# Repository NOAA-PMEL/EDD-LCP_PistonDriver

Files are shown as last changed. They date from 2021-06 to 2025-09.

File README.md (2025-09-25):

## Legal Disclaimer
### Software Disclaimer
*This repository is a software product and is not official communication 
of the National Oceanic and Atmospheric Administration (NOAA), or the 
United States Department of Commerce (DOC).  All NOAA GitHub project 
code is provided on an 'as is' basis and the user assumes responsibility 
for its use.  Any claims against the DOC or DOC bureaus stemming from 
the use of this GitHub project will be governed by all applicable Federal 
law.  Any reference to specific commercial products, processes, or services 
by service mark, trademark, manufacturer, or otherwise, does not constitute 
or imply their endorsement, recommendation, or favoring by the DOC. 
The DOC seal and logo, or the seal and logo of a DOC bureau, shall not 
be used in any manner to imply endorsement of any commercial product 
or activity by the DOC or the United States Government.*

### Hardware Disclaimer
*NOAA does not intend to patent this work worldwide. It may be used freely, but NOAA does not warrant its fitness for any use.*

*As a work of the United States Government, the associated schematics and software are in the public domain within the United States. Additionally, NOAA waives any potential copyright and related rights in the associated schematics and software worldwide through the Creative Commons Zero (CC0) 1.0 Universal Public Domain Declaration.*

# EDD-LCP_PistonDriver
Repository for LCP Piston Driver PCB design and firmware.

This repository is home to the piston driver PCB design and firmware for the low-cost-profiler project (likely to be renamed).

## State of this project
The LCP has been extensilivly tested and deployed in Puget Sound and the Bering Sea in Moored mode.  The mechanical design is complete, the electronics hardware needs a goround-up re-design for lower power consumption, decreased cost, and robustness.  The Firmware needs a ground up re-write for robustnuss and readability.  The piston board should be merged with the LCP-Control Board, and the seperate micro-controller elminated if possible.

# Branch
Master_gcc is the active branch and encompasses the most upto date version of the project 

# Low-Cost-Profiler
Low Cost Profiler for Oceanographic Monitoring

## Profiler System Diagram
```mermaid
graph LR;

    subgraph Low Cost Profiler

    MainController --- PistonController
    GPS --> MainController
    Pressure --> MainController
    Temperature --> MainController
    IMU --> MainController
    Accelerometer --> MainController
    subgraph Profiler Control
        MainController
        subgraph sensors
            Pressure
            Temperature
            GPS 
            IMU
            Accelerometer
        end

        IridiumSBD --- MainController
        subgraph Telemetry
        IridiumSBD
        end
    end

    subgraph Power Control ;
    Piston --> PistonController
    Encoder --> PistonController
    subgraph motion
    Encoder
    Piston
    end
    Batteries --> PistonController
    subgraph power
    Batteries
    end
    BatteryFuelGauge --> PistonController
    subgraph Sensor2
    BatteryFuelGauge     
    end
    end
    
    end
```

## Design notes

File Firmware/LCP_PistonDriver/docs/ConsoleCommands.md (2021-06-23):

# Console Command List

This document lists all of the user console commands, intended function, and associated errors.

## Console COM Connection
The console is found on Connector J1 of the LCP Piston Control PCB.  J1 is connected to UART UCA0 of the MSP430FR5989.  J1 was designed to be connected with a standard 3.3V FTDI USB-to-UART cable.

### Connection Info
| Description | Setting |
|---|---|
| Baudrate | 115200 |
| Data Bits | 8 |
| Parity | None |
| Stop Bits | 1 |

## Console
The user console is designed as a debuging and system integration test peripheral.  It is *not* designed
for use as the primary control port, and as such has a lower priority than the I2C port which *is* intended
for primary control between systems.

### Console Characteristics
When correctly connected to J1 over UART, the console terminal looks like:

>PISTxxxx>

where:<br>
>PIST is the LCP Piston Control designator <br>
>xxxx is the serial number of the Piston Controller <br>
> \> is terminal prompt

All commands are terminated with carriage return ('\r')\

___
### Command Set
---
#### Basic Commands
| Command | Description |
| --- | --- |
| help | List all commands |
| hello | Returns 'Hello from PISTxxxx!\r' |
| restart | Restart board (clear temporary values) |

---
#### LED Commands
| Command | Description | Key Name | Value |
|---|---|---|---|
| LED *name* *state* | Set commanded LED to requested state | GREEN or BLUE | ON, OFF or BLINK | 

---
#### System Information
| Command | Description | 
|---|---|
| ser | Display serial number |
| id | System ID (LCP-PPC) |
| ver | Firmware Version (major.minor.build) |
| report | Display report of system information |

---
#### GET/SET Commands 
The GET/SET commands read and write (respectively) the system control variables used to set the various states,
speeds, etc. The command structure is:

> get *key* 

OR

> set *key* *value*

* The *key* is the variable that the user wishes to read or write to.  
* The *value* is the value (int, float, string, etc.) the user wishes to write to the *key* variable

##### KEY/VALUE 
The following is a list of key/value that can be used with the *get* or *set* functions:

| **KEY** | **VALUE (type)** | **GET** | **SET** |  **DESCRIPTION** |
|---|---|---|---|---|
| vset | float | X | X | Volume Setpoint [in^3] |
| vtotal | float | X | | Current Total Volume [in^3] |
| vsmall | float | X |  | Current Volume of small piston [in^3] |
| vlarge | float | X |  | Current Volume of large piston [in^3] |
| vhouse | float | X |  | Housing Volume [in^3] | 
| asmall | float | X |  | Small piston area [in^2] | 
| alarge | float | X |  | Large piston area [in^2] |
| ltotal | float | X |  | Length of full piston [in] |
| lsmall | float | X |  | Length of small piston [in] |
| llarge | float | X |  | Length of large piston [in] |
| pmin | float | X | X | Piston Minimum Position [in] | 
| pmax | float | X | X | Piston Maximum Position [in] |
| prate | float | X |  | Piston rate, current [in/sec] |
| tdir | int | X |  | Piston travel direction, extension = 1, retraction = -1 |
| teng | bool | X |  | Travel engaged (halted=False, running=True) |
| tzero | bool | X |  | Travel position at full retraction (No=False, Yes=True) |
| tfull | bool | X |  | Travel position at full extension (No=False, Yes=True) |
| pidp | float | X | X | PID Coefficient (P) | 
| pidi | float | X | X | PID Coefficient (I) |
| pidd | float | X | X | PID Coefficient (D) | 
| user | string | X | X | User Name (default: **guest**) |
| level | int | X | X | Logging Level (0-Off, 1-Debug+, 2-Warning+, 3-Errors Only)|
| restart | None |  | X | Restart system |

---
The following list can be used if the username is set to **admin**

| **KEY** | **VALUE (type)** | **GET** | **SET** |  **DESCRIPTION** |
|---|---|---|---|---|
| utest | int | X | X | Test mode (read next section for description) |
| udir | int | X | X | User defined direction (extension = 1, retraction = -1) |
| ueng | bool | X | X| User defined power engaged (Off=False, On=True) |
| urate | float | X | X| User defined piston rate (approx) [in/sec] |
| ulset | float | X | X | User defined total length setpoint (in) |
| serial | string | X | X | User defined serial number |
| factory | string |  | X | Factory reset (string must be PMEL to be accepted) | 

##### RAM Commands
It is possible to read & write to the I2C command RAM space over the console.  Use the following syntax

> set *-r* *addr* *length* *value*

* *-r* Flag setting RAM location
* *addr* Address offset location (0x0Y00 - 0x0YFF) (Y=0,1,2)
* *length* Number of bytes to read/write (int)
* *value* Hex values to write (no 0x before hex string)

#### Test Modes
The following are the available test modes

| Mode | Test Description | 
|---|---|
| 0 | Test(s) OFF |
| 1 | Run to fully extended |
| 2 | Run to fully retracted |
| 3 | Run to half extension |
| 4 | Zero > Full, 1/2" increments |
| 5 | Full > Zero, 1/2" increments |
| 6 | Zero > Full > Zero, 1/2" increments |
| 7 | Zero > Full > Zero, loop until keystroke |
| 8 | Zero > Full > Zero, 1/2" increments, loop until keystroke |

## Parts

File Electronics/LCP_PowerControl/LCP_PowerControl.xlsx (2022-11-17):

Reference | Quantity | Value | Footprint | MPN
C1 | 1 | 1uF | Capacitor_SMD:C_0805_2012Metric | GCM21BC72A105KE36L
C14 C15 | 2 | 9pF | Capacitor_SMD:C_0603_1608Metric | CBR06C909BAGAC
C16 | 1 | 1000pF | Capacitor_SMD:C_0603_1608Metric | CL10B102KB8NNNC
C17 C18 C23 C25 | 4 | 10uF | Capacitor_SMD:C_1210_3225Metric | CL32B106KMVNNWE
C19 | 1 | 1uF | Capacitor_SMD:C_0603_1608Metric | CL10A105KB8NNNC
C2 C3 | 2 | 0.47uF | Capacitor_SMD:C_0805_2012Metric | 885012207102
C21 | 1 | 0.1uF | Capacitor_SMD:C_0603_1608Metric | GCM188R71H104KA57J
C20 C22 | 2 | 0.22uF | Capacitor_SMD:C_0603_1608Metric | C1608X7R1H224K080AE
C24 | 1 | 1.0uF | Capacitor_SMD:C_0603_1608Metric | CL10B105KP8NNNC
C26 C27 | 2 | 0.1uF | Capacitor_SMD:C_0402_1005Metric | GRM155R71A104KA01D
C28 C29 | 2 | 10uF | Capacitor_SMD:C_1206_3216Metric | CL31B106KPHVPNE
C30 | 1 | DNP | Capacitor_SMD:C_0603_1608Metric | DNP
C31 C32 C33 | 3 | 10uF | Capacitor_SMD:C_0805_2012Metric | GRM21BR61E106KA73L
C4 | 1 | CP | Capacitor_THT:CP_Radial_D12.5mm_P5.00mm | ECA-1HM102B
C5 C6 C9 C10 C11 C12 C13 | 7 | 0.1uF | Capacitor_SMD:C_0805_2012Metric | 885012207045
C7 | 1 | 0.022uF | Capacitor_SMD:C_0805_2012Metric | C2012X7R2E223K125AA
C8 | 1 | 10uF | Capacitor_SMD:CP_Elec_4x4.5 | EEE-HB1C100R
D1 D2 D3 D4 | 4 | 5.6V | Diode_SMD:D_SOD-323_HandSoldering | UDZ5V6B-7
D5 | 1 | D | Diode_SMD:D_SMA | SK53A-LTP
D6 | 1 | LED_BLUE | LED_SMD:LED_0805_2012Metric | APT2012LVBC/D
D7 | 1 | LED_GREEN | LED_SMD:LED_0805_2012Metric | APT2012SGC
F1 | 1 | 1A | Fuse:Fuse_Bourns_MF-RG650 | MF-R090
F3 | 1 | 250mA | Fuse:Fuse_Bourns_MF-RG650 | MF-R025
J1 | 1 | Conn_01x06 | Connector_PinSocket_2.54mm:PinSocket_1x06_P2.54mm_Vertical | 61300611121
J17 | 1 | Conn_01x02 | Connector_Molex:Molex_Micro-Fit_3.0_43045-0200_2x01_P3.00mm_Horizontal | 430450213
J18 | 1 | Conn_01x04 | Connector_Molex:Molex_Micro-Fit_3.0_43045-0400_2x02_P3.00mm_Horizontal | 430450413
J2 | 1 | Conn_01x05 | Connector_PinHeader_2.54mm:PinHeader_1x05_P2.54mm_Vertical | 61300511121
J3 J9 J10 J11 J12 | 5 | Conn_01x02 | Connector_Molex:Molex_Micro-Fit_3.0_43045-0212_2x01_P3.00mm_Vertical | 430450213
J5 | 1 | Conn_02x05_Odd_Even | Connector_PinSocket_1.27mm:PinSocket_2x05_P1.27mm_Vertical | 3220-10-0100-00
L1 | 1 | 12uH | Inductor_SMD:L_Bourns-SRN8040_8x8.15mm | SDR0805-120ML
L2 | 1 | 10uH | Inductor_SMD:L_Coilcraft_XAL1010 | XAL1010-103MEB
Q1 | 1 | DMG2305UX-7 | Package_TO_SOT_SMD:SOT-23 | DMG2305UX-7
R1 R2 | 2 | 4.42M | Resistor_SMD:R_0805_2012Metric | CRCW08054M42FKEA
R10 R22 | 2 | 10k | Resistor_SMD:R_0805_2012Metric | RNCP0805FTD10K0
R11 | 1 | 1.3k | Resistor_SMD:R_0805_2012Metric | RNCP0805FTD1K30
R12 | 1 | 2.0k | Resistor_SMD:R_0805_2012Metric | RNCP0805FTD2K00
R13 | 1 | 47k | Resistor_SMD:R_0805_2012Metric | CRGCQ0805F47K
R14 | 1 | 26.7k | Resistor_SMD:R_0402_1005Metric | RC0402FR-0726K7L
R16 | 1 | 51k | Resistor_SMD:R_0603_1608Metric | RC0603FR-0751KL
R17 | 1 | 22.1k | Resistor_SMD:R_0402_1005Metric | RMCF0402FT22K1
R15 R18 | 2 | 100k | Resistor_SMD:R_0402_1005Metric | RMCF0402FT100K
R19 | 1 | 9.09k | Resistor_SMD:R_0402_1005Metric | RT0402BRD079K09L
R20 | 1 | 1k | Resistor_SMD:R_0402_1005Metric | PFR05S-102-FNH
R21 | 1 | 470 | Resistor_SMD:R_0805_2012Metric | CRGCQ0805F470R
R23 R24 | 2 | 49.9 | Resistor_SMD:R_0805_2012Metric | RNCP0805FTD49R9
R3 | 1 | 200k | Resistor_SMD:R_0805_2012Metric | CRCW0805200KJNEA
R4 | 1 | 499k | Resistor_SMD:R_0805_2012Metric | RC0805FR-07499KL
R5 | 1 | 0.25 | Resistor_THT:R_Axial_Power_L48.0mm_W12.5mm_P55.88mm | RS010R2500FE73
R6 | 1 | 1k | Resistor_SMD:R_0805_2012Metric | RNCP0805FTD1K00
R7 R8 | 2 | 150 | Resistor_SMD:R_0805_2012Metric | RNCP0805FTD150R
R9 | 1 | 750 | Resistor_SMD:R_0805_2012Metric | CRG0805F750R
RN1 RN2 | 2 | R_Pack02 | Resistor_SMD:R_Array_Concave_2x0603 | EXB-V4V472JV
RN4 RN5 | 2 | 4.7k | Resistor_SMD:R_Array_Concave_2x0603 | EXB-V4V472JV
SW1 | 1 | SW_Push | Button_Switch_SMD:SW_SPST_TL3305A | PTS810 SJS 250 SMTR LFS
U1 | 1 | MAX17205 | Package_DFN_QFN:DFN-14-1EP_3x3mm_P0.4mm_EP1.78x2.35mm | MAX17205G+T
U2 | 1 | DRV8874 | Package_SO:HTSSOP-16-1EP_4.4x5mm_P0.65mm_EP3.4x5mm_Mask3x3mm_ThermalVias | DRV8874PWPR
U3 | 1 | MSP430FR5989 | Package_QFP:LQFP-64_10x10mm_P0.5mm | MSP430FR5989IPMR
U4 | 1 | LMR50410 | Package_TO_SOT_SMD:SOT-23-6_Handsoldering | LMR50410YQDBVRQ1
U5 | 1 | LM61460 | Converter_DCDC:TI_RJR0014A | LMQ61460AFSQRJRRQ1
Y1 | 1 | 32.768kHz | Crystal:Crystal_SMD_3215-2Pin_3.2x1.5mm | ABS07-32.768KHZ-9-T
e1 Q2 | 2 | PMBF170,215 | Package_TO_SOT_SMD:SOT-23 | PMBF170,215

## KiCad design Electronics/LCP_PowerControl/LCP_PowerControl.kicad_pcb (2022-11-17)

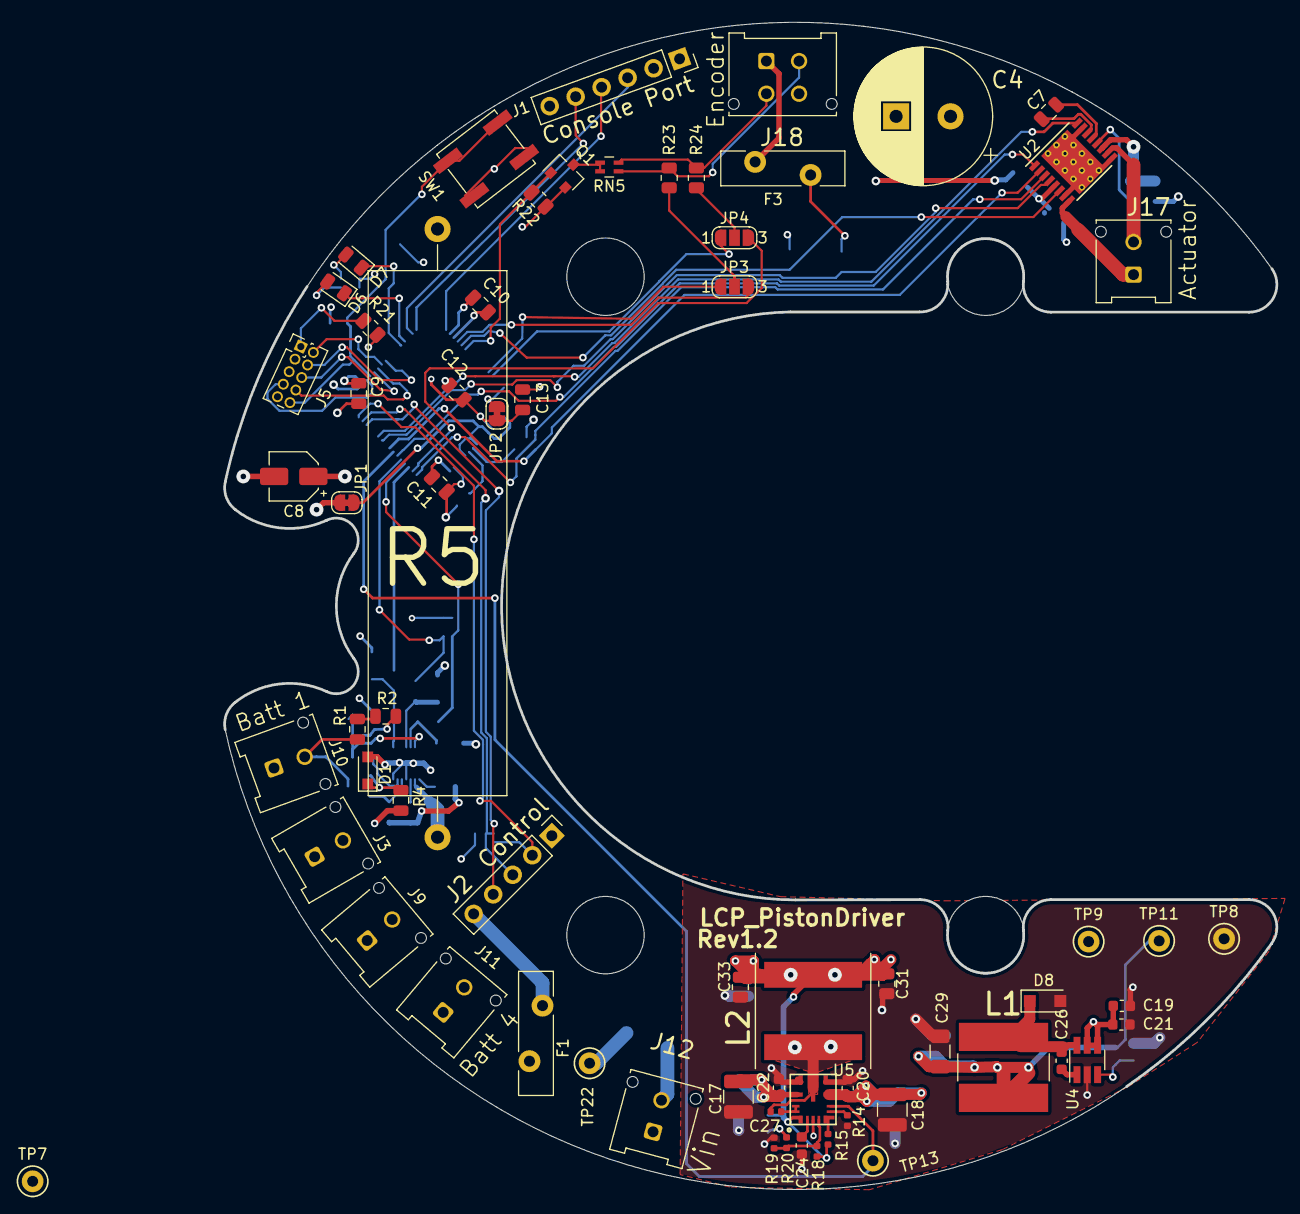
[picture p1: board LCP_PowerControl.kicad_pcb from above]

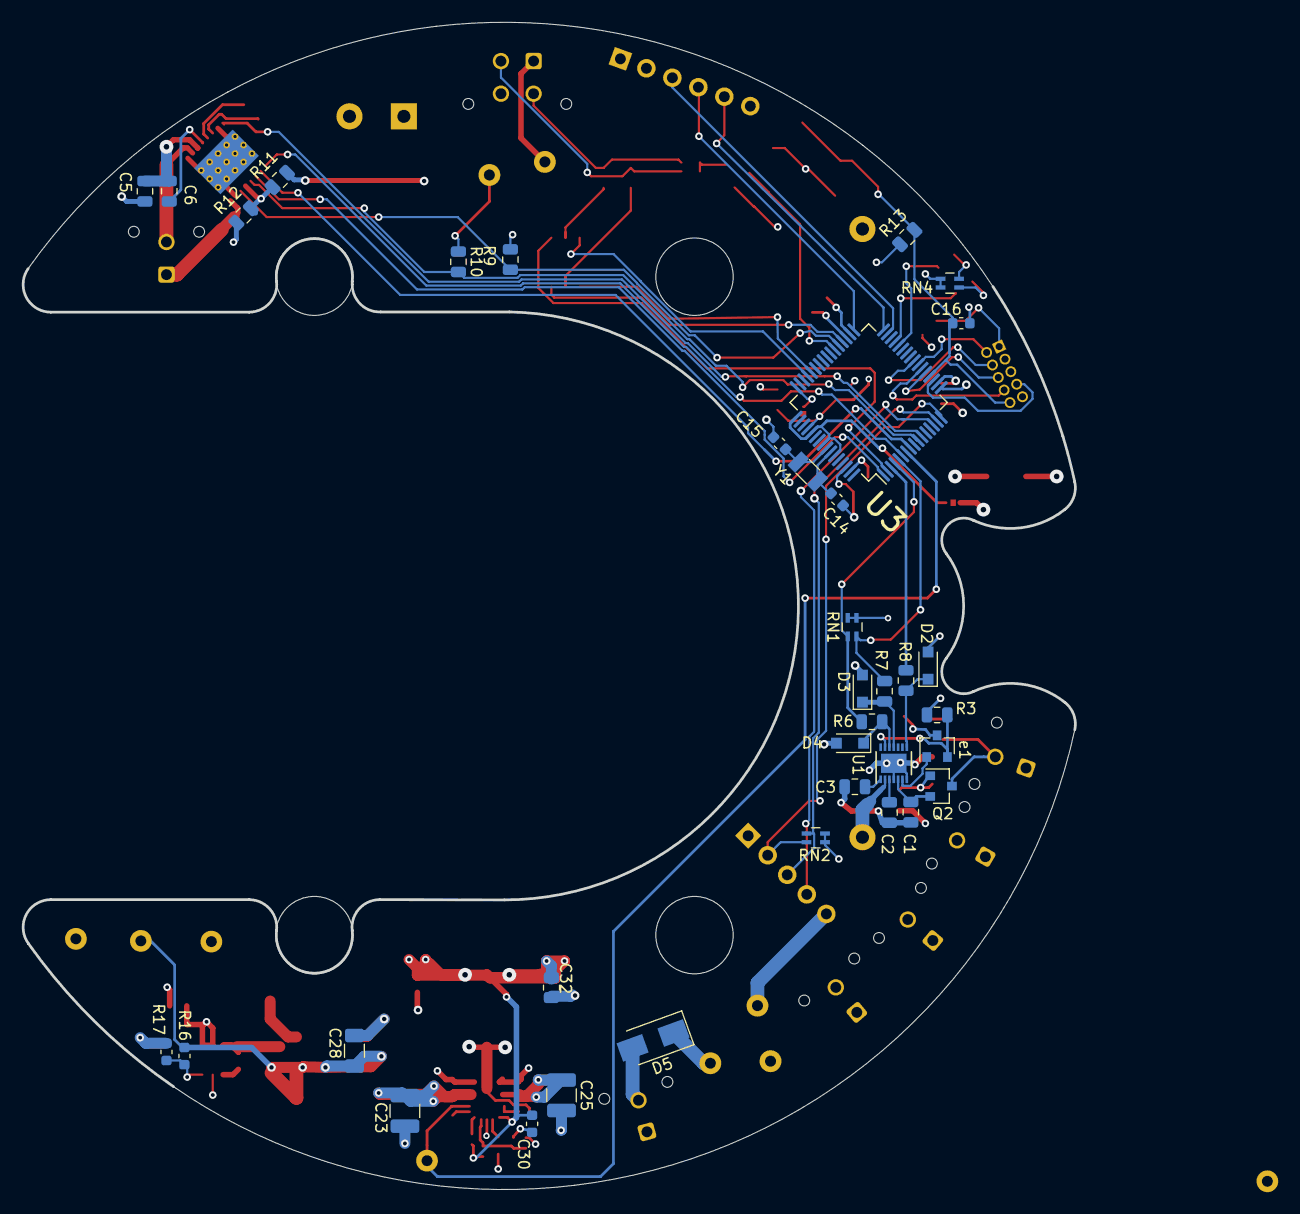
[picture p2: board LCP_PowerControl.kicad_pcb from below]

Board: 4 copper layers, 96.7 x 107.2 mm, 103 parts (36 on the bottom side), 76 nets.

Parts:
C1: 1uF; C_0805_2012Metric
C2, C3: 0.47uF; C_0805_2012Metric
C4: CP; CP_Radial_D12.5mm_P5.00mm
C5, C6, C9, C10, C11, C12, C13: 0.1uF; C_0805_2012Metric
C7: 0.022uF; C_0805_2012Metric
C8: 10uF; CP_Elec_4x4.5
C14, C15: 9pF; C_0603_1608Metric
C16: 1000pF; C_0603_1608Metric
C17, C18, C23, C25: 10uF; C_1210_3225Metric
C19: 1uF; C_0603_1608Metric
C20, C22: 0.22uF; C_0603_1608Metric
C21, C26: 0.1uF; C_0603_1608Metric
C24: 1.0uF; C_0603_1608Metric
C27: 0.1uF; C_0402_1005Metric
C28, C29: 10uF; C_1206_3216Metric
C30: DNP; C_0603_1608Metric
C31, C32, C33: 10uF; R_0805_2012Metric
D1, D2, D3, D4: 5.6V; D_SOD-323_HandSoldering
D5: D; D_SMA
D6: LED_BLUE; LED_0805_2012Metric
D7: LED_GREEN; LED_0805_2012Metric
D8: RB060M-60TR; D_SOD-123F
F1: 1A; Fuse_Bourns_MF-RG650
F3: 250mA; Fuse_Bourns_MF-RG650
J1: Conn_01x06; PinSocket_1x06_P2.54mm_Vertical
J2: Conn_01x05; PinHeader_1x05_P2.54mm_Vertical
J3, J9, J10, J11, J12, J17: Conn_01x02; Molex_Micro-Fit_3.0_43045-0212_2x01_P3.00mm_Vertical
J5: Conn_02x05_Odd_Even; PinHeader_2x05_P1.27mm_Vertical
J18: Conn_01x04; Molex_Micro-Fit_3.0_43045-0412_2x02_P3.00mm_Vertical
JP1, JP2: SolderJumper_2_Bridged; SolderJumper-2_P1.3mm_Bridged_RoundedPad1.0x1.5mm
JP3, JP4: SolderJumper_3_Open; SolderJumper-3_P1.3mm_Open_RoundedPad1.0x1.5mm_NumberLabels
L1: 12uH; L_Bourns-SRN8040_8x8.15mm
L2: 10uH; L_Coilcraft_XAL1010
Q1: DMG2305UX-7; SOT-23
Q2: ZVN4106FTA; SOT-23
R1, R2: 4.42M; R_0805_2012Metric
R3: 200k; R_0805_2012Metric
R4: 499k; R_0805_2012Metric
R5: 0.25; R_Axial_Power_L48.0mm_W12.5mm_P55.88mm
R6: 1k; R_0805_2012Metric
R7, R8: 150; R_0805_2012Metric
R9: 750; R_0805_2012Metric
R10, R22: 10k; R_0805_2012Metric
R11: 1.3k; R_0805_2012Metric
R12: 2.0k; R_0805_2012Metric
R13: 47k; R_0805_2012Metric
R14: 26.7k; R_0402_1005Metric
R15, R18: 100k; R_0402_1005Metric
R16: 51k; R_0603_1608Metric
R17: 15k; R_0603_1608Metric
R19: 9.09k; R_0402_1005Metric
R20: 1k; R_0402_1005Metric
R21: 470; R_0805_2012Metric
R23, R24: 49.9; R_0805_2012Metric
RN1, RN2: R_Pack02; R_Array_Concave_2x0603
RN4, RN5: 4.7k; R_Array_Concave_2x0603
SW1: SW_Push; SW_SPST_EVQP0
TP7, TP8, TP9, TP11, TP13, TP22: TestPoint; TestPoint_Keystone_5000-5004_Miniature
U1: MAX17205; DFN-14-1EP_3x3mm_P0.4mm_EP1.78x2.35mm
U2: DRV8874; HTSSOP-16-1EP_4.4x5mm_P0.65mm_EP3.4x5mm_Mask3x3mm_ThermalVi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
U3: MSP430FR5989; LQFP-64_10x10mm_P0.5mm
U4: BD9G102G-LB; SOT-23-6_Handsoldering
U5: LM61460; TI_RJR0014A
Y1: 32.768kHz; Crystal_SMD_3215-2Pin_3.2x1.5mm
e1: ZVN4106FTA; SOT-23

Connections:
+3V3: C8.1, C9.1, C10.1, C11.1, C12.1, C13.1, C28.1, C29.1, F3.2, JP2.1, L1.2, Q1.2, R10.1, R11.1, R13.1, R16.1, R21.1, R22.1, RN1.3, RN1.4, RN2.3, RN2.4, RN4.3, RN4.4, TP11.1, U3.18, U3.35, U3.52, U3.63
+12V: C4.1, C5.1, C6.1, C30.1, C31.1, C32.1, C33.1, L2.2, R15.2, R18.2, TP9.1, U2.11, U5.1
+BATT: C17.1, C18.1, C19.1, C20.1, C21.1, C22.1, C23.1, C25.1, D5.1, F1.1, J3.2, J9.2, J10.2, J11.2, Q2.3, R1.1, R4.1, TP7.1, TP22.1, U4.4, U4.5, U5.8, U5.12
/Actuator Connector/ACTUATOR_POWER+: J17.1, U2.8
/Actuator Connector/ACTUATOR_POWER-: J17.2, U2.10
/Actuator Connector/HALL_EFFECT_V+: F3.1, J18.1
/Battery Input/BATT_V-: J3.1, J9.1, J10.1, J11.1, J12.1, R5.2, U1.2
/Console/CONSOLE_PWR: J1.3, U3.31
/Console/CONSOLE_RX: J1.5, U3.32
/Console/CONSOLE_TX: J1.4, U3.33
/Control Board Connection/CONTROL_EN: J2.4, U3.14
/Control Board Connection/CONTROL_SCL: J2.2, RN2.2, U3.16
/Control Board Connection/CONTROL_SDA: J2.3, RN2.1, U3.15
/Debug/DEBUG_LED_1: D7.1, U3.28
/Debug/DEBUG_LED_2: D6.1, U3.29
/Microcontroller/BM_IRQ: R8.1, U3.3
/Microcontroller/BM_SCL: R7.1, RN1.2, U3.5
/Microcontroller/BM_SDA: R6.1, RN1.1, U3.4
/Microcontroller/ENCODER_CH_A: J18.2, R23.1, RN5.1
/Microcontroller/ENCODER_CH_B: J18.3, R24.2, RN5.2
/Microcontroller/SBWTCK: J5.7, U3.19
/Microcontroller/TCK: J5.4, U3.24
/Microcontroller/TDI: J5.8, U3.22
/Microcontroller/TDO: J5.6, U3.21
/Microcontroller/TMS: J5.2, U3.23
/Microcontroller/~RESET: C16.1, J5.10, R13.2, SW1.1, U3.20
/Piston Driver/V_ref: R11.2, R12.1, U2.5
ADC2: R9.1, U2.6, U3.37
ESICI0: JP3.1, U3.44
ESICI1: JP4.1, U3.45
GND: C1.2, C2.2, C3.2, C4.2, C5.2, C8.2, C9.2, C10.2, C11.2, C12.2, C13.2, C14.1, C15.1, C16.2, C17.2, C18.2, C19.2, C20.2, C21.2, C22.2, C23.2, C24.2, C25.2, C28.2, C29.2, C31.2, C32.2, C33.2, D1.2, D2.2, D3.2, D4.2, D8.2, J1.1, J2.1, J5.3, J5.5, J5.9, J18.4, JP1.1, R3.2, R5.1, R9.2, R12.2, R14.2, R17.2, R19.1, SW1.2, TP8.1, U1.4, U1.7, U1.15, U2.7, U2.9, U2.15, U2.17, U3.17, U3.34, U3.62, U4.2, U5.3, U5.9, U5.11
GNDA: JP1.2, U3.49, U3.53, U3.56, U3.59
unnamed: C1.1, Q2.2, U1.5
unnamed: C2.1, U1.3
unnamed: C3.1, U1.1
unnamed: C6.2, U2.12
unnamed: C7.1, U2.13
unnamed: C7.2, U2.14
unnamed: C14.2, U3.58, Y1.1
unnamed: C15.2, U3.57, Y1.2
unnamed: C24.1, U5.2
unnamed: C26.1, D8.1, L1.1, U4.6
unnamed: C26.2, U4.1
unnamed: C27.1, U5.13, U5.14
unnamed: C27.2, L2.1, U5.10
unnamed: C30.2, R20.2
unnamed: D1.1, Q2.1, R4.2
unnamed: D2.1, R8.2, U1.8
unnamed: D3.1, R7.2, U1.11
unnamed: D4.1, R6.2, U1.12
unnamed: D5.2, J12.2
unnamed: D6.2, RN4.1
unnamed: D7.2, RN4.2
unnamed: F1.2, J2.5
unnamed: J5.1, R21.2
unnamed: JP2.2, U3.48
unnamed: JP3.2, R23.2
unnamed: JP4.2, R24.1
unnamed: Q1.3, RN5.3, RN5.4
unnamed: R1.2, R2.1
unnamed: R2.2, e1.3
unnamed: R3.1, U1.13, e1.2
unnamed: R14.1, U5.6
unnamed: R15.1, U5.5
unnamed: R16.2, R17.1, U4.3
unnamed: R18.1, R19.2, R20.1, U5.4
unnamed: U1.6, e1.1
P1.1: Q1.1, R22.2, U3.38
P1.3: JP3.3, U3.36
P1.4: JP4.3, U3.2
P2.5: TP13.1, U3.7, U5.7
P2.6: U2.2, U3.8
P4.3: U2.3, U3.1
P5.0: R10.2, U2.4, U3.10
P5.1: U2.16, U3.11
PWM_TB0.3: U2.1, U3.6

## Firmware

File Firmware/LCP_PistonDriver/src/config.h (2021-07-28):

#ifndef CONFIG_H_
#define CONFIG_H

/** Motor Driver Mode Selection */
//#define MD_CONFIG_MODE_PHEN
#define MD_CONFIG_MODE_PWM

#define FIRMWARE        ("v0.1")
#define SYS_ID          ("LCPPST01")

/** Volume Movement Settings */
#define SYS_VOLUME_DIFF_MAX     ( 0.030 )

/** Piston Settings */
#define SYS_SMALL_PISTON_DIAMETER         ( 2.25f )
#define SYS_SMALL_PISTON_MAX_LENGTH       ( 6.00f )
#define SYS_LARGE_PISTON_DIAMETER         ( 4.50f ) 
#define SYS_LARGE_PISTON_MAX_LENGTH       ( 6.0f )
#define SYS_HOUSING_DIAMETER                ( 4.88f )
#define SYS_HOUSING_LENGTH                  ( 35.0f )

/** Encoder Settings */
#define SYS_ENCODER_MIN_COUNT_DEFAULT   ( 0 ) 
#define SYS_ENCODER_MAX_COUNT_DEFAULT   ( 72609 )
#define SYS_ENCODER_LENGTH_DEFAULT      ( 11.6875 )

/*******************************************************************************
 * Extended Scan Interface Settings
 ******************************************************************************/

// The section provides all the define used in this application for
// gInterruptFlags

#define FLUSH_COUNTER_REGISTERS			        BITF
#define FLUSH_DEBUG_REGISTERS					BITE
//#define 				BITD
//#define 				BITC
//#define 				BITB
//#define 				BITA
//#define 				BIT9
//#define 				BIT8
//#define 				BIT7
//#define 				BIT6
//#define 				BIT5
//#define 				BIT4
#define DEBUG_REGISTER_FLUSH_ENABLED		                BIT3
#define PERIODIC_COUNTER_FLUSH_ENABLED		                BIT2
#define START_CONFIG_ESI_MODULE				BIT1
#define COMM_CAL_DONE 						BIT0

#define ESICHX_PORT				GPIO_PORT_P9
#define ESICH0_PIN				GPIO_PIN0
#define ESICH1_PIN				GPIO_PIN1
#define ESICH2_PIN				GPIO_PIN2
#define ESICH3_PIN				GPIO_PIN3




//---- ESIOSC frequency setting based user selection for ACLK frequency

#define ACLK_FREQUENCY_IN_HZ				32768


#define ESIOSC_DEFAULT  4800000/ACLK_FREQUENCY_IN_HZ
#define ESIOSC_3MHz     3000000/ACLK_FREQUENCY_IN_HZ
#define ESIOSC_4MHz     4000000/ACLK_FREQUENCY_IN_HZ
#define ESIOSC_5MHz     5000000/ACLK_FREQUENCY_IN_HZ
#define ESIOSC_6MHz     6000000/ACLK_FREQUENCY_IN_HZ
#define ESIOSC_7MHz     7000000/ACLK_FREQUENCY_IN_HZ
   
   
#define RECAL_TIME_OUT				8192
#define TIMER_RECALIBRATION_SELECTION				TIMER_A0_BASE
#define TIMER_RECALIBRATION_CLK_SOURCE				TIMER_A_CLOCKSOURCE_ACLK
#define TIME_TO_RECAL				61440
#define TIME_TO_RECAL_REPEAT						4
#define RECALIBRATION_TIMER_VECTOR_0				TIMER0_A0_VECTOR


#ifdef TEST
#define PIN0        ( 1u << 0 )
#define PIN1        ( 1u << 1 )
#define PIN2        ( 1u << 2 )
#define PIN3        ( 1u << 3 )
#define PIN4        ( 1u << 4 )
#define PIN5        ( 1u << 5 )
#define PIN6        ( 1u << 6 )
#define PIN7        ( 1u << 7 )

#define PORT_P1     ( 1u)
#define PORT_P2     ( 2u )
#define PORT_P3     ( 3u )
#define PORT_P4     ( 4u )
#define PORT_P5     ( 5u )
#define PORT_P6     ( 6u )
#define PORT_P7     ( 7u )
#define PORT_P8     ( 8u )
#define PORT_P9     ( 9u )

#define DEFAULT_MODULE_FUNCITON     ( 0 )
#define PRIMARY_MODULE_FUNCTION    ( 1 )
#define SECONDARY_MODULE_FUNCTION    ( 2 )
#define TERNARY_MODULE_FUNCTION    ( 3 )

#else
#define PIN0        ( GPIO_PIN0 )
#define PIN1        ( GPIO_PIN1 )
#define PIN2        ( GPIO_PIN2 )
#define PIN3        ( GPIO_PIN3 )
#define PIN4        ( GPIO_PIN4 )
#define PIN5        ( GPIO_PIN5 )
#define PIN6        ( GPIO_PIN6 )
#define PIN7        ( GPIO_PIN7 )


#define PORT_P1     ( GPIO_PORT_P1 )
#define PORT_P2     ( GPIO_PORT_P2 )
#define PORT_P3     ( GPIO_PORT_P3 )
#define PORT_P4     ( GPIO_PORT_P4 )
#define PORT_P5     ( GPIO_PORT_P5 )
#define PORT_P6     ( GPIO_PORT_P6 )
#define PORT_P7     ( GPIO_PORT_P7 )
#define PORT_P8     ( GPIO_PORT_P8 )
#define PORT_P9     ( GPIO_PORT_P9 )

#define DEFAULT_MDOULE_FUNCTION     ( 0 )
#define PRIMARY_MODULE_FUNCTION     ( GPIO_PRIMARY_MODULE_FUNCTION )
#define SECONDARY_MODULE_FUNCTION   ( GPIO_SECONDARY_MODULE_FUNCTION )
#define TERNARY_MODULE_FUNCTION     ( GPIO_TERNARY_MODULE_FUNCTION )

#endif

#endif

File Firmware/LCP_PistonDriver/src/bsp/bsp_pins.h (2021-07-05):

#ifndef _BSP_PINS_H_
#define _BSP_PINS_H_

#include <stdint.h>
#include <stdbool.h>

#include "config.h"
#ifndef TEST
#include <driverlib/driverlib.h>
#endif






typedef struct {
    uint8_t port;
    uint16_t pin;
    bool mode;        /*<< Pin Mode 1=Output, 0=Input */
    bool configured;  /**< Is the port configured 0=NO, 1=YES */
    uint8_t function;   /**< 0=Normal, 1=Primary, 2=Secondary, 3=Ternary */
    bool inverted;       /**< Invert the output */

    /** Input Options */
    uint8_t pullups;     /**< Needs resistors 0=No, 1=Pull-ups, 2=Pull-Downs */
    bool interrupt;      /**< Is there an interrupt attached? 0=No, 1=Yes */
    bool interruptEdge;  /**< Interrupt Edge 0=Low To High, 1=High to Low */

    /** Input Value */
    volatile bool inputValue;  /**< Value of Input */
}driverlib_gpio_cfg_t;

#define DEFAULT_MODULE_FUNCTION ( 0 )

#define GPIO_SET_AS_INPUT   ( 0 )
#define GPIO_SET_AS_OUTPUT  ( 1 )



/***********************************************
 * LED Pins
 **********************************************/
/***********************************************
 * LED0 pin: Green LED
 **********************************************/
#if DEBUG && DEBUG_LED
#define BSP_GPIO_GREEN_LED_PORT     ( PORT_P3 )
#define BSP_GPIO_GREEN_LED_PIN      ( PIN6 )  
extern const driverlib_gpio_cfg_t g_BSP_GPIO_GREEN_LED;
#endif

/***********************************************
 * LED1 pin: RED LED
 **********************************************/
#if DEBUG && DEBUG_LED
#define BSP_GPIO_BLUE_LED_PORT     ( PORT_P3 )
#define BSP_GPIO_BLUE_LED_PIN      ( PIN7 )  
extern const driverlib_gpio_cfg_t g_BSP_GPIO_BLUE_LED;
#endif

/***********************************************
 * Debug UART Pins
 **********************************************/
/***********************************************
 * Debug UART Rx Pin
 **********************************************/
#define BSP_UART_DEBUG_RX_PORT             ( PORT_P3 )
#define BSP_UART_DEBUG_RX_PIN              ( PIN5 )
extern const driverlib_gpio_cfg_t BSP_UART_DEBUG_RX;

/***********************************************
 * Debug UART Tx Pin
 **********************************************/
#define BSP_UART_DEBUG_TX_PORT             ( PORT_P3 )
#define BSP_UART_DEBUG_TX_PIN              ( PIN4 )
extern const driverlib_gpio_cfg_t BSP_UART_DEBUG_TX;


/***********************************************
 * Console UART Pins
 **********************************************/
/***********************************************
 * Console UART Rx Pin
 **********************************************/
#define BSP_UART_CONSOLE_RX_PORT             ( PORT_P2 )
#define BSP_UART_CONSOLE_RX_PIN              ( PIN1 )
extern const driverlib_gpio_cfg_t BSP_UART_CONSOLE_RX;

/***********************************************
 * Console UART Tx Pin
 **********************************************/
#define BSP_UART_CONSOLE_TX_PORT             ( PORT_P2 )
#define BSP_UART_CONSOLE_TX_PIN              ( PIN0 )
extern const driverlib_gpio_cfg_t BSP_UART_CONSOLE_TX;



/***********************************************
 * 12V Enable Pin
 **********************************************/
#define BSP_GPIO_12V_ENABLE_PORT        ( PORT_P2 )
#define BSP_GPIO_12V_ENABLE_PIN         ( PIN5 )
extern const driverlib_gpio_cfg_t g_BSP_GPIO_12V_ENABLE;


/***********************************************
 * Battery Management Pins
 **********************************************/
/***********************************************
 * Battery Management IRQ Pin
 **********************************************/
#define BSP_GPIO_BM_IRQ_PORT            ( PORT_P1)
#define BSP_GPIO_BM_IRQ_PIN             ( PIN5)
extern const driverlib_gpio_cfg_t g_BSP_GPIO_BM_IRQ;

/***********************************************
 * Battery Management I2C SDA Pin
 **********************************************/
#define BSP_I2C_BM_SDA_PORT             ( PORT_P1 )
#define BSP_I2C_BM_SDA_PIN              ( PORT_P6 )
extern const driverlib_gpio_cfg_t g_BSP_I2C_BM_SDA;

/***********************************************
 * Battery Management I2C SCL Pin
 **********************************************/
#define BSP_I2C_BM_SCL_PORT             ( PORT_P1 )
#define BSP_I2C_BM_SCL_PIN              ( PORT_P7 )
extern const driverlib_gpio_cfg_t g_BSP_I2C_BM_SCL;


/***********************************************
 * Control Communications Pins
 **********************************************/
/***********************************************
 * Control Enable Pin
 **********************************************/
#define BSP_GPIO_CONTROL_IRQ_PORT            ( PORT_P3)
#define BSP_GPIO_CONTROL_IRQ_PIN             ( PIN0)
extern const driverlib_gpio_cfg_t g_BSP_GPIO_CONTROL_IRQ;

/***********************************************
 * Control I2C SDA Pin
 **********************************************/
#define BSP_I2C_CONTROL_SDA_PORT             ( PORT_P3 )
#define BSP_I2C_CONTROL_SDA_PIN              ( PIN1 )
extern const driverlib_gpio_cfg_t g_BSP_I2C_CONTROL_SDA;

/***********************************************
 * Control I2C SCL Pin
 **********************************************/
#define BSP_I2C_CONTROL_SCL_PORT             ( PORT_P3 )
#define BSP_I2C_CONTROL_SCL_PIN              ( PIN2 )
extern const driverlib_gpio_cfg_t g_BSP_I2C_CONTROL_SCL;

/***********************************************
 * H-Bridge (Motor Driver) Pins
 **********************************************/
/***********************************************
 * H-Bridge Enable Pin
 **********************************************/
#define BSP_GPIO_MD_ENABLE_PORT            ( PORT_P2)
#define BSP_GPIO_MD_ENABLE_PIN             ( PIN4)
extern const driverlib_gpio_cfg_t g_BSP_GPIO_MD_ENABLE;

/***********************************************
 * H-Bridge Phase Pin
 **********************************************/
#define BSP_GPIO_MD_PH_PORT            ( PORT_P2)
#define BSP_GPIO_MD_PH_PIN             ( PIN6)
extern const driverlib_gpio_cfg_t g_BSP_GPIO_MD_PH;

/***********************************************
 * H-Bridge Sleep Pin
 **********************************************/
#define BSP_GPIO_MD_SLEEP_PORT            ( PORT_P4)
#define BSP_GPIO_MD_SLEEP_PIN             ( PIN3)
extern const driverlib_gpio_cfg_t g_BSP_GPIO_MD_SLEEP;

/***********************************************
 * H-Bridge Fault Pin
 **********************************************/
#define BSP_GPIO_MD_FAULT_PORT            ( PORT_P5)
#define BSP_GPIO_MD_FAULT_PIN             ( PIN0)
extern const driverlib_gpio_cfg_t g_BSP_GPIO_MD_FAULT;

/***********************************************
 * H-Bridge Mode Pin
 **********************************************/
#define BSP_GPIO_MD_PMODE_PORT            ( PORT_P5)
#define BSP_GPIO_MD_PMODE_PIN             ( PIN1)
extern const driverlib_gpio_cfg_t g_BSP_GPIO_MD_PMODE;

/***********************************************
 * H-Bridge ADC IPROPI Pin
 **********************************************/
#define BSP_GPIO_MD_IPROPI_PORT            ( PORT_P1)
#define BSP_GPIO_MD_IPROPI_PIN             ( PIN2)
extern const driverlib_gpio_cfg_t g_BSP_GPIO_MD_IPROPI;

/***********************************************
 * Encoder Pins
 **********************************************/
/***********************************************
 * Encoder Pin A
 **********************************************/
#define BSP_GPIO_ENCODER_A_PORT           ( PORT_P1)
#define BSP_GPIO_ENCODER_A_PIN            ( PIN3)
extern const driverlib_gpio_cfg_t g_BSP_GPIO_ENCODER_A;

/***********************************************
 * Encoder Pin B
 **********************************************/
#define BSP_GPIO_ENCODER_B_PORT           ( PORT_P1)
#define BSP_GPIO_ENCODER_B_PIN            ( PIN4)
extern const driverlib_gpio_cfg_t g_BSP_GPIO_ENCODER_B;

#endif

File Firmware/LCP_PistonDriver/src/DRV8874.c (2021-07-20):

#include "DRV8874.h"
#include "logging.h"
#include <stdio.h>

float _read_adc12_volts(void) ;
uint16_t _calculate_pwm(uint8_t percent);


static uint16_t speed_fwd = 0;
static uint16_t speed_rev =0;

void DRV8874_init(void) {

 BSP_GPIO_Init(&g_BSP_GPIO_MD_SLEEP);
 
 BSP_GPIO_Init(&g_BSP_GPIO_MD_FAULT);
 BSP_GPIO_Init(&g_BSP_GPIO_MD_PMODE);
 BSP_GPIO_Init(&g_BSP_GPIO_MD_IPROPI);
 BSP_GPIO_Init(&g_BSP_GPIO_MD_ENABLE);
 BSP_GPIO_Init(&g_BSP_GPIO_MD_PH);
 
#ifdef DRV8874_NO_PWM
 BSP_GPIO_Clear(&g_BSP_GPIO_MD_PMODE);
 
#else 
 BSP_GPIO_Set(&g_BSP_GPIO_MD_PMODE);
#endif
 
 
 DRV8874_enable();
 // PWM Settings 
 // EN = TB0.3
 // PH = TB0.5
}



void DRV8874_enable( void ) 
{
  Log.Debug("Enabling DRV8874");
  BSP_12V_On();
}


void DRV8874_disable( void ) 
{
  Log.Debug("Disabling DRV8874");
  BSP_12V_Off();
}

void DRV8874_forward( uint8_t percent )
{
  char temp[80];
  speed_rev = 0;
  BSP_GPIO_Set(&g_BSP_GPIO_MD_SLEEP);
#ifdef DRV8874_NO_PWM
  BSP_GPIO_Set(&g_BSP_GPIO_MD_ENABLE);
  BSP_GPIO_Clear(&g_BSP_GPIO_MD_PH);
#else
  BPS_PWM_SetPWM(0,0);
  uint16_t target = _calculate_pwm(percent);
  int16_t inc = 0;
  
  if( target == speed_fwd)
  {
    Log.Debug("Already at target speed");
    return;
  }
  else if(target > speed_fwd)
  {
    inc = 1;
  }else {
    inc = -1;
  }
  
  sprintf(temp, "Setting DRV8874 FORWARD at %u%%, pwm = %u", percent, target);
  Log.Debug(temp);
  do {
    BPS_PWM_SetPWM(1, speed_fwd);  
    __delay_cycles(1000);
    speed_fwd += inc;
  } while (target != speed_fwd);
  
  
#endif

}



void DRV8874_reverse( uint8_t percent ) 
 {
  char temp[80];
  speed_fwd = 0;
  BSP_GPIO_Set(&g_BSP_GPIO_MD_SLEEP);
#ifdef DRV8874_NO_PWM
  BSP_GPIO_Set(&g_BSP_GPIO_MD_ENABLE);
  BSP_GPIO_Set(&g_BSP_GPIO_MD_PH);
#else
   BPS_PWM_SetPWM(1,0);
  uint16_t target = _calculate_pwm(percent);
  int16_t inc = 0;
 
  if( target == speed_rev)
  {
    Log.Debug("Already at target speed");
    return;
  }
  else if(target > speed_rev)
  {
    inc = 1;
  }else {
    inc = -1;
  }
 sprintf(temp, "Setting DRV8874 FORWARD at %u%%, pwm = %u", percent, target);
 Log.Debug(temp);
  do {
    BPS_PWM_SetPWM(0, speed_rev);  
    __delay_cycles(1000);
    speed_rev += inc;
  } while (target != speed_rev);

#endif 

}




void DRV8874_stop( void ) {
#ifdef DRV8874_NO_PWM
  BSP_GPIO_Clear(&g_BSP_GPIO_MD_PH);
  BSP_GPIO_Clear(&g_BSP_GPIO_MD_ENABLE);
#else
  BPS_PWM_SetPWM(0,0);
  BPS_PWM_SetPWM(1,0);
#endif  
  BSP_GPIO_Clear(&g_BSP_GPIO_MD_SLEEP);
  
  speed_fwd = 0;
  speed_rev = 0;
  Log.Debug("DRV8874 Stopped");
}

float DRV8874_read_current( void )
{

//  /** Convert to amps */
  float v_ipropi = 0.0f;
  float i_propi = 0.0f;
  
  for(uint8_t i=0; i<25; i++)
  {
    v_ipropi += _read_adc12_volts();
  }
  v_ipropi = v_ipropi / 10.0f;
  i_propi = v_ipropi / 750.0f;
  i_propi = i_propi / 444e-6;
  
  return i_propi;
}


float _read_adc12_volts(void) { 

  return BSP_ADC12_Read_voltage();
}
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

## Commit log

2020-06-13 Adding current state of schematic for Power Controller
    [BatteryInput.sch, Console.sch, Control.sch, LCP_PowerControl.kicad_pcb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]
2020-06-16 Adding libraries and recent changes
    [ActuatorConnector.sch, BatteryInput.sch, Console.sch, Control.sch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]
2020-06-17 Aiming for rev 0.1 complete
    [ActuatorConnector.sch, BatteryInput.sch, Console.sch, Control.sch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]
2020-07-22 KiCad Layout
    Component and Traces finished. Need a look over. Will work on Silkscreen
    after.
    JTAG Connector. Should pin 1 be pulled up w/ 470Ohm resistor similar to
    other designs? Also TDI and TMI signals are connected, is this correct?
    [BatteryInput.sch, LCP_PowerControl.kicad_pcb, Microcontroller.sch, PowerMonitoring.sch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]
2020-09-04 Arduino commit for Hall Effect Sensor.
    Arduino code for Trinket M0
2020-09-08 Position request within 0.005 inches working
    [PowerMonitoring.sch]
2020-10-14 LCP_PowerControl Rev1
    Board layout in Kicad.
    Gerbers.
    BOM
    [BatteryInput.sch, Debug.sch, LCP_PowerControl-B_Cu.gbr, LCP_PowerControl-B_Mask.gbr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]
2020-12-10 Adding first pass at LCP Piston Driver Board bringup.
    Compiles, sys_init passes, and LEDs blink
2020-12-12 I2C working.
    Both B0 & B1 I2C transmitting. B0 wiring seems to be coupled on both lines.
2020-12-16 Adding BSP files.
    All current files for BSP for basic bringup operations
2020-12-18 DMA and ADC12 working.
    The DMA is now tied to ADC12 for behind-the-scenes transfer of ADC voltage.
2020-12-23 Rev1
    Removed test points. Cleaned up unnecessary traces. Fixed electrical issues #1-#7
    [BatteryInput.sch, Console.sch, Control.sch, Debug.sch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]
2020-12-23 BOM Update
    Updated MPNs on components to match supplies as well as correcting some resistor values
    [ActuatorConnector.sch, BatteryInput.sch, Console.sch, Control.sch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]
2021-02-01 Rev 1 Update
    Issues #9-#13 fixed
    Rev 1 Gerbers & BOM Ready
    [Debug.sch, LCP_PowerControl-B_Cu.gbr, LCP_PowerControl-B_Mask.gbr, LCP_PowerControl-B_Paste.gbr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]
2021-03-09 Adding selection for GPIO encoder read.
    Adding P1.3/4 for encoder A/B read
    [Microcontroller.sch]
2021-03-09 adding power control to pull-ups.
    Adding ability to power on/off the pull-ups on the encoder
    [Microcontroller.sch, PositionSensing.sch, PowerMonitoring.sch]
2021-03-09 Rev1.1 Gerber Upload
    Included 3way open solder jumps to choose control of Encoder channels of hall effect sensor
    [LCP_PowerControl-B_Cu.gbr, LCP_PowerControl-B_Mask.gbr, LCP_PowerControl-B_Paste.gbr, LCP_PowerControl-B_SilkS.gbr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]
2021-06-22 Adding memory map excel sheet
    [MemoryMap.xlsx]
2021-06-23 Adding full unit test of P002
    [MemoryMap.xlsx]
2021-06-28 Simplifying structure
    [MemoryMap.xlsx]
2021-06-28 Fixing struct with single bytes.
    Was using lists, but that was bad bad bad. Now using slice to deal with single, works much better
    [MemoryMap.xlsx]
2021-06-29 LCP Command I2C Interface major update.
    Adding commands to read/write to all addresses. memory map looks complete, too
    [MemoryMap.xlsx]
2021-06-30 Console commands and memory call updates
    [MemoryMap.xlsx]
2021-07-07 Adding runto full calibaration.
    Calibration now runs to full and saves max count into struct. Report updated with encoder values
2021-07-07 Fixed current measurement.
    Now showing about 1 amp per read during run
2021-07-07 whoa.
    Lot going on here. Can move to position (from zero, but reverse count is still screwed up).
    Tried to do a variable speed move to postition, but it's not working correctly. Good for today
2022-03-22 LCP PowerControl Board Update
    [ActuatorConnector.sch, Debug.sch, LCP_PowerControl-B_Cu.gbr, LCP_PowerControl-B_Mask.gbr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]
2022-11-17 Reestablishing top page of heirarchical pages
    [LCP_PowerControl.sch]
